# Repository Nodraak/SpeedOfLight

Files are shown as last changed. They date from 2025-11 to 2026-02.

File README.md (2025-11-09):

# Speed of light

*Reenactment of experiment(s) to measure the speed of light.*

Following a [video by AlphaPhenix in 2018](https://www.youtube.com/watch?v=YMO9uUsjXaI), where he redo Fizeau's experiement, I set out to reenact the experiement myself.
After some research, it seems to me that Foucault's experiement is easier to perform and will give a more precise value, while using a somehow similar technique.

(Incomplete) history of speed of light measurements from [Wikipedia](https://en.wikipedia.org/wiki/Speed_of_light#Measurement):

| Scientist | Experiment                                | Year | Value measured (accuracy)                  |
|-----------|-------------------------------------------|------|--------------------------------------------|
| Rømer     | Jupiter vs Io timing                      | 1676 | Earth's orbit's diameter / 22 min          |
| Bradley   | Aberration of light from a distant star   | 1729 | Sun to the Earth distance / 8 min 12 sec   |
| Fizeau    | Time of flight with a toothed wheel       | 1848 | 313 274 304 m/s (4.5%)                     |
| Foucault  | Time of flight with a mirror              | 1862 | 298 000 000 m/s (0.6%)                     |
| Cornu     | Refinement of Fizeau's                    | 1872 | 300 400 000 m/s (0.2%)                     |
| Michelson | Refinement of Foucault's                  | 1879 | 299 944 000 m/s (0.05%)                    |

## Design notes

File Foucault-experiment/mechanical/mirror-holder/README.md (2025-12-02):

# Mirror Holder

## Introduction

*Piece to hold the mirror and mount it on the motor, 70x40 mm.*

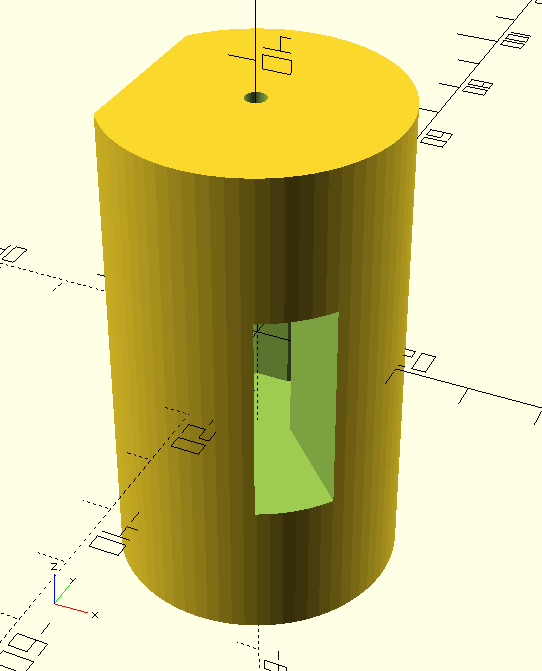
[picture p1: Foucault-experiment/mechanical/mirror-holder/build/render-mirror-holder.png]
Finished piece
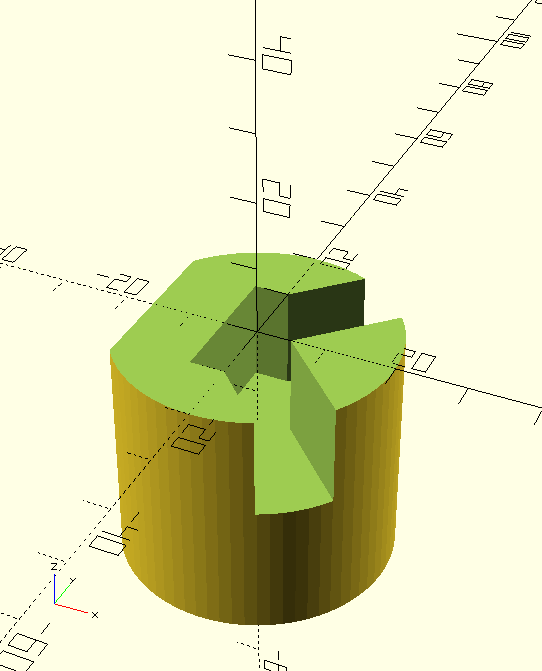
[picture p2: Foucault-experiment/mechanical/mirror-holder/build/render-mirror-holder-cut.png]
Half cut to view the inside
 

The holder will rotate quickly (10-100 RPM).
Therefore, the mirror must be well secured so that it does not fly away.
The best is to take advantage of the centrifugal force to keep it in place.
This leads to an unbalanced piece, which must then be carefully balanced with a notch of a very specific depth.
To help with balancing, the piece is as full as possible, and only a small path for the laser is carved through.

## Initial design with ChapGPT

An initial design was done with ChapGPT to quickly get started with a rough shape and to work around OpenScad's syntax which I'm not familiar with.

Prompt:

```
Write an openscad script code:

* Main: Create a main, vertical cylinder d=30 mm, h=60 mm
* Motor holes: Subtract at each end (top and bottom), a cylinder d=3 mm, h=15 mm
* Mirror: Subtract at the middle, a rectangles LxD=10x20 mm and h=30 mm
* Laser path:
    * Subtract two horizontal rectangles
        * W=sqrt(5**2+5**2) mm, L=20 mm
        * Each oriented +/- 45 deg horizontally compared to the previous middle rectangle
        * One end of the rectangle should be on the center of the main cylinder, the other end should go towards the outside
    * Subtract similar rectangles
        * But with the end +/- 5 mm horizontally from the center of the main cylinder
* Rear balancing: Subtract a rectangle H=60 mm, W=30 mm
    * Similar to the "Laser path" subtractions, but on the other side (horizontally)
    * Its center should be W/2+10 mm from the center of the Main cylinder

A few requests:

* Write only the code and nothing else.
* Do not add comments for obvious things, but do add a comment for each step above.
* Use variables as needed for constants.
* Add "$fn = 60;" at the top.
```

## 3D printing

* OpenScad
    * Render
    * Export as STL
* Ultimaker Cura
    * Layer height: 0.2 mm
    * Density: 40% (TBD: 30-50%?)
    * Pattern: Tri Hexagon (TBD: Cubic, Tri-Hexagonal, Grid, Triangle?)
    * Speed: 50 mm/sec
    * -> Print time: 4.5h (first PoC: 1.5h)

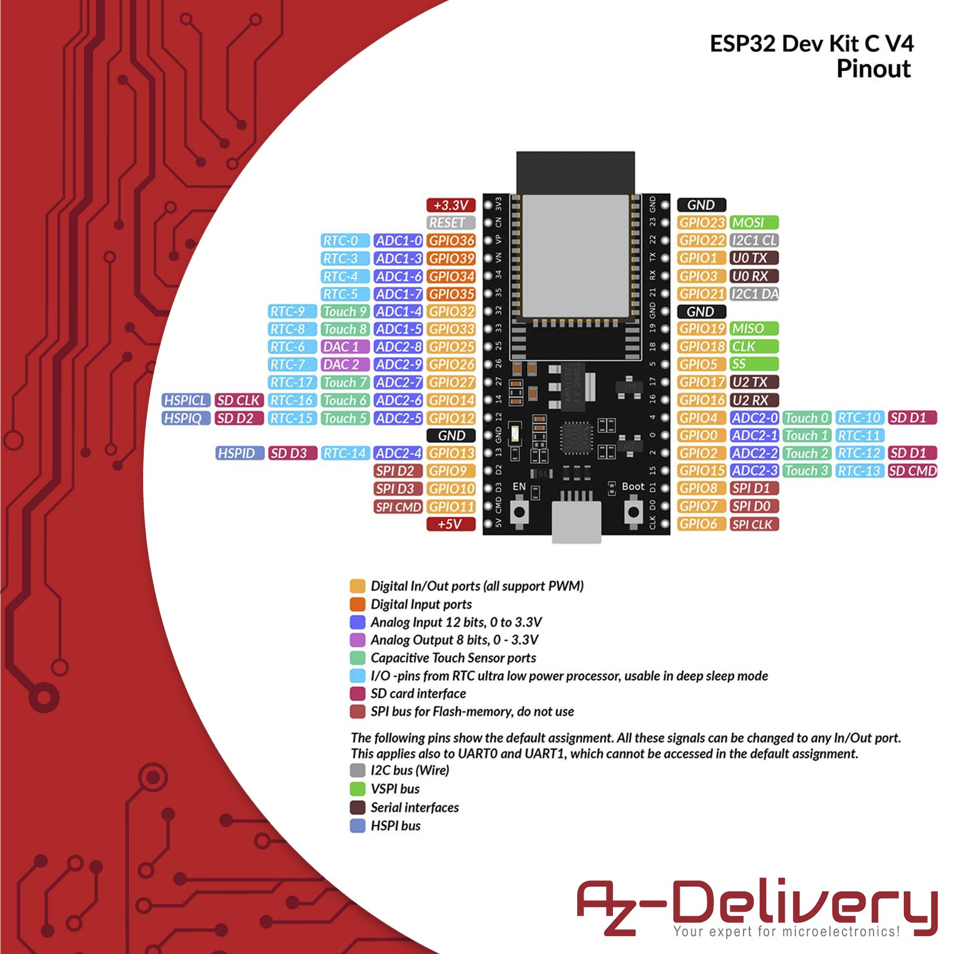
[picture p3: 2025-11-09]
Foucault-experiment/electrical/datasheets/pinout.jpg

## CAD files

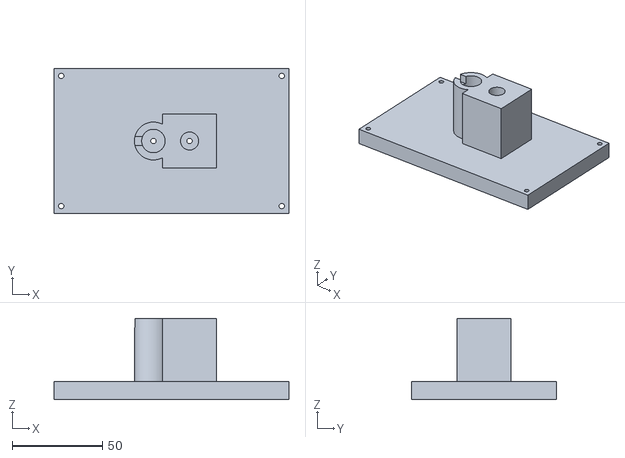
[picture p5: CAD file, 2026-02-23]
Foucault-experiment/mechanical/main-assembly/build/top-assembly.stl
130.0 x 80.0 x 45.0

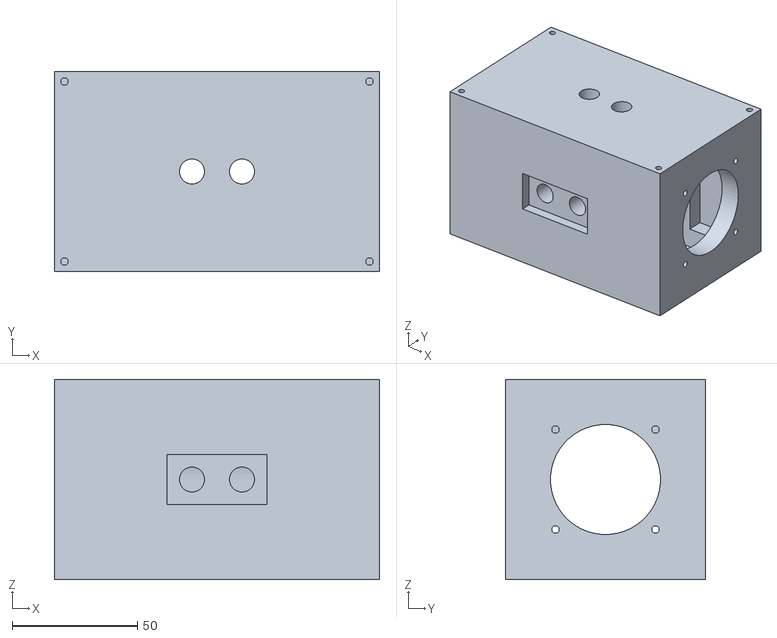
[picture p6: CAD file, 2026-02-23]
Foucault-experiment/mechanical/main-assembly/build/bottom-assembly.stl
130.0 x 80.0 x 80.0

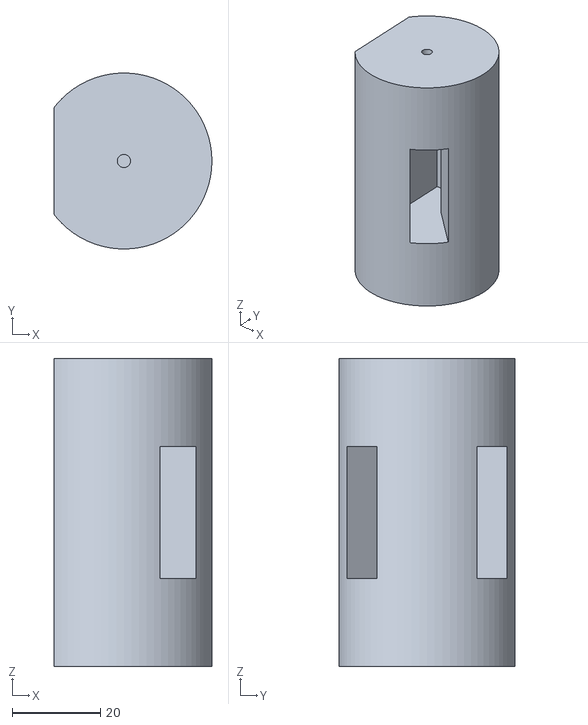
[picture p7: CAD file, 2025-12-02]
Foucault-experiment/mechanical/mirror-holder/build/mirror-holder.stl
35.9 x 40.0 x 70.0

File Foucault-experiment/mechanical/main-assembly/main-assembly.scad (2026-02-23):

/*
    # Main assembly

    Initial ChatGPT prompt:

    ```
    Write an openscad script code:

    * Create a rectangular box w=170 x d=80 x h=80. Write w=170 as 10+30+90+30+10
    * Difference a cylinder, centered in the rectangular box, of diameter=5+40+5
    * Difference a smaller rectangular box, depth=5+40+5, height=(80-(5+40+5))/2 + 5 + 5, just below the cylinder
    * Difference 4 holes on each side of the rectangular box, around the cylinder hole. diameter=3, d=10 further away than the cylinder's diameter.
    * Difference a vertical shaft (cylinder) from the rectangular box; d=10, centered on the depth axis, at an horizontal position of 10+30+90*1/4
    * Difference an horizontal shaft (cylinder) from the rectangular box; d=10, centered on the vertical axis, at an horizontal position of 10+30+90*1/4
    * Difference a vertical shaft (cylinder) from the rectangular box; d=10, centered on the depth axis, at an horizontal position of 10+30+90*3/4
    * Difference an horizontal shaft (cylinder) from the rectangular box; d=10, centered on the vertical axis, at an horizontal position of 10+30+90*3/4

    A few requests:

    * Write only the code and nothing else.
    * Do not add comments for obvious things, but do add a comment for each step above.
    * Use variables as needed for constants.
    * Add "$fn = 60;" at the top.
    ```
*/

// number of segments ; overrides $fa (minimum angle) and $fn (minimum size)
$fn = $preview ? 32 : 64;

//
// Constants
//

// main_box_w = 10 + 30 + 90 + 30 + 10;  // wall + motor + spinning cylinder + motor + wall
main_box_w = 10 + 30-10 + 70 + 30-10 + 10;  // wall + motor-wall + spinning cylinder + motor-wall + wall
main_box_h = 80;

main_cyl_d = 2 + 40 + 2; // 5 mm margin around spinning cylinder

motor_cube_depth = 20;
motor_cube_side = 60;

motor_screw_hole_pos = 40;
motor_screw_hole_d = 3;

// light_shaft_pos = 90*1/4;
light_shaft_pos = 40*1/4;
light_shaft_d = 10;
light_shaft_d_2 = 3;

laser_l = 45;  // 35 + some margin for the wire
laser_d = 13;  // 12 is too small
laser_box_d = laser_d + 2*4;

camera_pos = 40*1/4;
camera_holder_side = 30;
camera_holder_height = 45;

//
// Top assembly
//

module top_assembly() {
    translate([0, 0, main_box_h/2]) {
        // main plate
        difference() {

            // Create main plate
            translate([-main_box_w/2, -main_box_h/2, 0])
                cube([main_box_w, main_box_h, 10]);

            // 4 resting slots
            translate([0, 0, -main_box_h/2])
                bottom_assembly();

            // Vertical shaft at -1/4
            translate([-light_shaft_pos, 0, 0])
                cylinder(d = light_shaft_d_2, h = main_box_h + 2, center = true);

            // Vertical shaft at +1/4
            translate([+light_shaft_pos, 0, 0])
                cylinder(d = light_shaft_d_2, h = main_box_h + 2, center = true);

            // 4 screw holes - top
            for (x_offset = [-(main_box_w/2-5+1), +main_box_w/2-5+1])
                for (y_offset = [-(main_box_h/2-5+1), +main_box_h/2-5+1])
                    translate([x_offset, y_offset, 5])
                        cylinder(d = motor_screw_hole_d, h = 10+1, center = true);
        }

        // laser
        difference() {
            // laser holder
            translate([-light_shaft_pos, 0, laser_l/2])
                cylinder(d = laser_box_d, h = laser_l, center = true);

            // laser hole
            translate([-light_shaft_pos, 0, laser_l/2])
                cylinder(d = laser_d, h = laser_l+1, center = true);

            // wire
            translate([-light_shaft_pos-laser_box_d/2, 0, laser_l])
                cube([laser_box_d, 5, 2*5], center = true);
        }

        // camera
        difference() {
            // main block
            translate([+camera_pos, 0, laser_l/2])
                cube([camera_holder_side, camera_holder_side, camera_holder_height], center = true);

            // view hole
            translate([+camera_pos, 0, laser_l/2])
                cylinder(d = light_shaft_d, h = camera_holder_height+1, center = true);

            // laser hole
            translate([-light_shaft_pos, 0, laser_l/2])
                cylinder(d = laser_d, h = laser_l+1, center = true);
        }
    }
}

//
// Bottom assembly
//

module bottom_assembly() {
    difference() {

        // Create main rectangular box
        cube([main_box_w, main_box_h, main_box_h], center = true);

        rotate([0, 90, 0]) {
            // Difference main centered horizontal cylinder
            cylinder(d = main_cyl_d, h = main_box_w + 2, center = true);

            // centered horizontal rectangular box below cylinder
            translate([0, -main_cyl_d/2, -(main_box_w/2 - 10)])
                cube([main_box_h/2 + 1, main_cyl_d, main_box_w - 2*10]);

            // Sides motors attachement - cube
            translate([0, 0, -main_box_w/2 + 10 + motor_cube_depth/2 - 1])
                cube([motor_cube_side, motor_cube_side, motor_cube_depth], center = true);
            translate([0, 0, main_box_w/2 - 10 - motor_cube_depth/2])
                cube([motor_cube_side, motor_cube_side, motor_cube_depth], center = true);

            // 4 screw holes - on each side around cylinder hole
            for (x_offset = [-main_box_w/2, +main_box_w/2])
                for (y_offset = [-motor_screw_hole_pos/2, +motor_screw_hole_pos/2])
                    for (z_offset = [-motor_screw_hole_pos/2, +motor_screw_hole_pos/2])
                        translate([z_offset, y_offset, x_offset])
                            cylinder(d = motor_screw_hole_d, h = 2*10+1, center = true);
        }

        // Vertical shaft at -1/4
        translate([-light_shaft_pos, 0, 0])
            cylinder(d = light_shaft_d, h = main_box_h + 2, center = true);
        // Horizontal shaft at -1/4
        translate([-light_shaft_pos, -main_box_h/2, 0])
            rotate([90, 0, 0])
                cylinder(d = light_shaft_d, h = main_box_h + 2, center = true);

        // Vertical shaft at +1/4
        translate([+light_shaft_pos, 0, 0])
            cylinder(d = light_shaft_d, h = main_box_h + 2, center = true);
        // Horizontal shaft at +1/4
        translate([+light_shaft_pos, -main_box_h/2, 0])
            rotate([90, 0, 0])
                cylinder(d = light_shaft_d, h = main_box_h + 2, center = true);

        // resting slot - front
        translate([0, -main_box_h/2, 0])
            cube([40, 2*5, 20], center = true);

        // 4 resting slots - top
        for (x_offset = [-(main_box_w/2-5+1), +main_box_w/2-5+1])
            for (y_offset = [-(main_box_h/2-5+1), +main_box_h/2-5+1])
                translate([x_offset, y_offset, main_box_h/2-5])
                    cylinder(d = motor_screw_hole_d, h = 10+1, center = true);

        // cutout - side
        // translate([50, 0, 0])
        //     cube([100, 100, 100], center = true);

        // cutout - front
        // translate([0, -50, 0])
        //     cube([200, 100, 100], center = true);
    }
}

//
// Main
//

top_assembly();
bottom_assembly();

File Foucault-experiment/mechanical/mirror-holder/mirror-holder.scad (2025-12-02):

/*
    Mirror holder
*/

$fn = 72;

echo("==========");

//
// Helpers
//

function r2d(r) = r * 180 / 3.14159;
function d2r(d) = d * 3.14159 / 180;

pi_deg = acos(-1);
echo("pi_deg", pi_deg);

delta = 99;

//
// Constants
//

d_main = 40; // arbitrary
r_main = d_main / 2;

mirror_L = 10; // space
mirror_D = 22; // spec
mirror_H = 30; // spec

d_hole = 3; // spec
h_hole = 12.5; // spec
h_hole_margin = 2.5 + 5;

h_main = mirror_H + 2 * (h_hole + h_hole_margin);
echo("h_main", h_main);

laser_W = sqrt(5*5 + 5*5);
laser_L = delta;
laser_offset = 5;

rear_cap_h = 4.12; // manual optim COG
rear_W = d_main;
rear_H = h_main + delta;

// rear_cap_h 4.15 = COG base estimated 1.01, reality 1.03
// => better rear_cap_h 4.12 (-0.006)

//
// Main cylinder
//

difference() {
    cylinder(h = h_main, d = d_main, center = true);

    // Motor holes
    m_h = mirror_H/2 + h_hole_margin + h_hole/2;
    translate([0, 0, m_h]) cylinder(h = h_hole+1, d = d_hole, center = true);
    translate([0, 0, -m_h]) cylinder(h = h_hole+1, d = d_hole, center = true);

    // Mirror
    cube([mirror_L, mirror_D, mirror_H], center = true);

    // Laser path - center
    rotate([0, 0, 45]) translate([0, -laser_W/2, -mirror_H/2]) cube([laser_L, laser_W, mirror_H]);
    rotate([0, 0, -45]) translate([0, -laser_W/2, -mirror_H/2]) cube([laser_L, laser_W, mirror_H]);

    // Laser path - offset
    translate([0, laser_offset, 0])
        rotate([0, 0, 45]) translate([0, -laser_W/2, -mirror_H/2]) cube([laser_L, laser_W, mirror_H]);
    translate([0, -laser_offset, 0])
        rotate([0, 0, -45]) translate([0, -laser_W/2, -mirror_H/2]) cube([laser_L, laser_W, mirror_H]);

    // Rear balancing
    translate([-rear_W-r_main+rear_cap_h, -rear_W/2, -rear_H/2]) cube([rear_W, rear_W, rear_H]);

    // DEBUG: cut in half
    // translate([-50, -50, 0])
    //    cube([100, 100, 100]);
}

//
// Check COG
//

// cog_mirror
cog_mirror = -1.36;

// cog_base
theta_deg = 2*acos((r_main -rear_cap_h)/r_main );
// The centroid x of the remaining shape (signed toward the side opposite the removed cap)
cog_base = 2 * r_main * sin(theta_deg / 2)^3 / (3 * (3.14159 - 0.5*(d2r(theta_deg)-sin(theta_deg))));
echo("cog_base", cog_base);

// cog_base = 1.03;

// result
cog_global = (2 * (h_hole + h_hole_margin) * cog_base + mirror_H * cog_mirror) / h_main;

echo("Estimated COG:", cog_global);

echo("==========");

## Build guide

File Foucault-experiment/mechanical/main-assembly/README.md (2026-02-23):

# Main Assembly (Top + Bottom pieces)

## Introduction

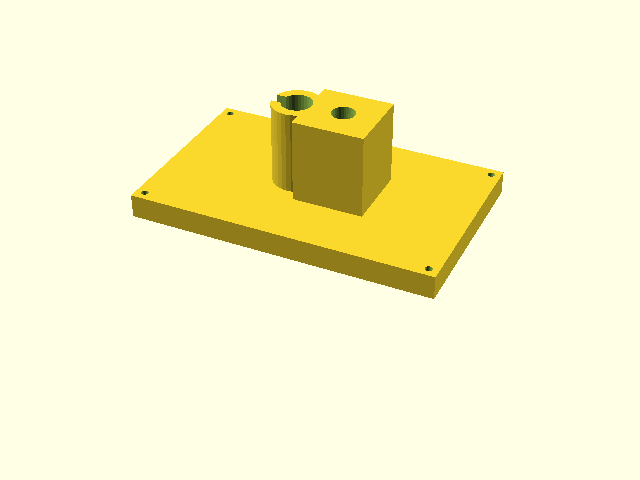
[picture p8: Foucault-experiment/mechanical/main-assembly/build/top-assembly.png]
Top assembly
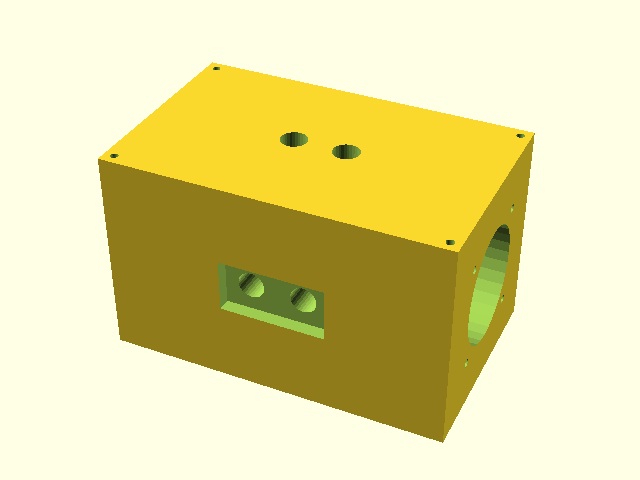
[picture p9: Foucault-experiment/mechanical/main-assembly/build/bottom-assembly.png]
Bottom assembly


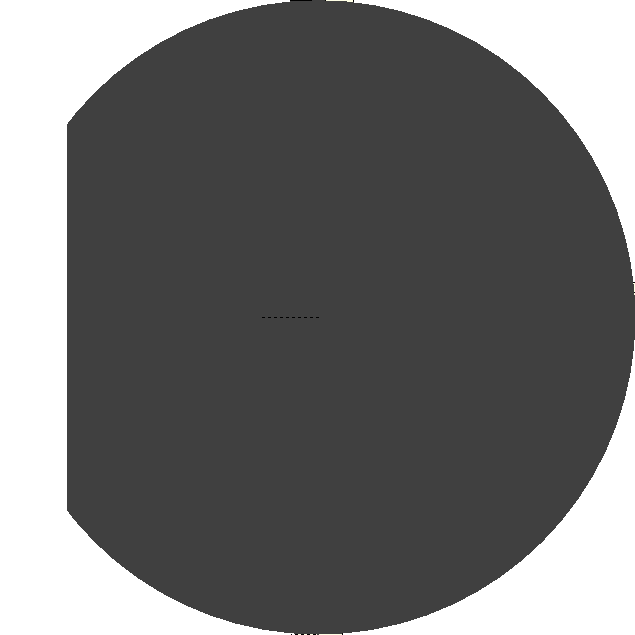
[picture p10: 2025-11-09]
Foucault-experiment/mechanical/mirror-holder/build/cog-slice-mirror-base-40-4.15.png

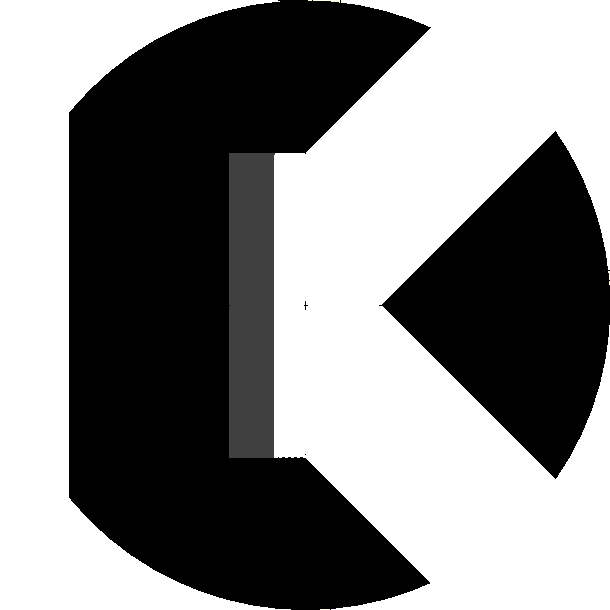
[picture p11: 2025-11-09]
Foucault-experiment/mechanical/mirror-holder/build/cog-slice-mirror-laser.png

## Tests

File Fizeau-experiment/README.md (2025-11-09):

# Fizeau's Experiment

*Some preliminary notes on Fizeau's experiment.*

## Laser

* Power: 5 mW
* Divergence: TBD

Safety:

* MPE = W/cm2 = safe
* Fully open pupil = 0.39 cm2
* MPE = 1 mW/cm2

## Distance and timing

300 000 000 m/s = 300 m/us

2 *  150 m =>  1 us
2 * 1.5 km => 10 us
2 * 8.0 km => 50 us

* Mueggelsee: 2 * 3.4 km
* Maerchenland: 2 * 1.5 km
* Kanal: 2 * 1.5 km
* Treptower: 2 * 1.0 km
* Havel: 2 * 3.5 km
* Saatwinkler Damm: 2 * 3.8 km

* Lehnitzsee: 2 * 2.0 km

* Trebeurden 1: 2 * 1.0 km
* Trebeurden 2: 2 * 3.7 km
* Trebeurden 3: 2 * 8.0 km

## Wheel

* Fizeau: 720 teeth / 15-50 rps
* AlphaPhenix: 140 teeth wheel (10 cm?) / 2-10 k rpm = 40-200 rps
    * => 10-50 k teeth/sec

* 10 k mm / sec = 1 mm / 100 us
* 50 k mm / sec = 1 mm /  20 us

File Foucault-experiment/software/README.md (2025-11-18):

# Software

## Introduction

Functions:

* Control the motor/ESC
    * Input from stdin: 1-100 k RPM
    * Create the PWM
        * 50 Hz: 20 ms idle, 1-2 ms signal
        * Precision: 1 % (10 us = 2 400 clock ticks at 240 MHz)
* Measure the actual RPM
    * Read the diode (analog) and detect discontinuity in the signal
    * 100 k RPM, 100 samples / rotation = 16 000 samples/sec = 60 us / sample
    * At 240 MHz, that's 15 000 clock ticks / sample
    * Print result at 1 Hz: RPM count, min/max duration between two discontinuities (for quality check)

## Arduino IDE for ESP32

azdelivery esp32 devkitc v4

CPU: Xtensa dual-core 32-bit LX6 microprocessor, 240 MHz
Memory: 520 KiB RAM
ADC: 2 × 12-bit SAR ADCs, up to 18 channels, with four levels of attenuation

https://github.com/tombenke/darduino

* Select Tools > Board > Boards Manager from the Arduino IDE menus to open the "Boards Manager" view in the left side panel.
* Scroll down through the list of boards platforms until you see the "esp32 by Espressif Systems" entry.
* Click the "INSTALL" button at the bottom of the entry.
* Wait for the installation to finish.

```
I need a C code to run on an azdelivery esp32 devkitc v4, via the Arduino IDE, with the following functions:

* Control the motor/ESC
    * Input from stdin: read stdin, parse an int between 1 000 and 100 000 (RPM)
    * Create the PWM:
        * Digital output
        * (50 Hz: 20 ms idle, 1-2 ms signal)
        * Precision: 1 % (10 us = 2 400 clock ticks at 240 MHz)
            * Can we implement it in the main loop? Do we need to use IRQs? Are they timers or builtin PWM controller on the ESP32?
    * Dont forget the arming sequence of the ESC
* Measure the actual RPM
    * Read the diode signal (analog input) and detect discontinuity in the signal to detect one rotation
        * In oder to do that in a reliable way, we can use an adaptive threshold:
        * Prepare an array of say, 256 values initialised to 0
        * Each time a value is read, increment the corresponding cell
        * After a 1 second cycle, find out the median value
        * Use this median value as the threshold for the next 1 sec cycle
        * Keep track of when we are in or out of reading a signal, to not count multiple times a given signal (wait for it to go back down below the threshold)
    * Measure per-sample timing (ISR execution time profiling) with a 1024 array (histogram), with 1 us per cell (1-1000 us)
        * Print at 1 Hz statistics: 10 deciles values
    * Also measure rotation duration with a 1024 items array (scale it so that index 512 corresponds to the expect duration at the currently configured ESC RPM, and index 0 and 1023 correspond to x1/10 and x10 this value)
    * Precision: 100 k RPM, 100 samples / rotation = 170 000 samples/sec = 6 us / sample
        * (At 240 MHz, that's 15 000 clock ticks / sample)
        * Same question again: can we implement it in the main loop? Do we need to use IRQs? Are they timers or builtin PWM controller on the ESP32?
    * Print the result at 1 Hz: RPM count, the threshold value, and other statistics as needed
* Use pin 32 for the PWM and 33 for the ADC input
```

## Example output (on Linux)

```
$ ./a.out

+---------------------------------+
| Project F - Foucault experiment |
+---------------------------------+

nod_pwm_init: pin=32 freq=50
nod_pwm_write_us: pin=32 freq=50 duty_us=1000
nod_pwm_write_duty: pin=32 duty=0
nod_adc1_init: ch=5
nod_mutex_init
nod_pwm_write_us: pin=32 freq=50 duty_us=1000
nod_pwm_write_duty: pin=32 duty=0
nod_timer_init: frequency=1000000 alarm_value=16000

cmd_rpm =   1000 RPM ; rev dur =  62500 us
meas_rpm =   1980 RPM ; rev dur =  30303 us
threshold_index = 1510 [0-4096] = 1.843 V
/--- sample_hist
| sample_total_count=  1824
| min=     0 | med=   518 | max=  2973
| ds=    184    268    347    433    518    596    685    762    838   2973
\---
/--- rev_duration
| sample_total_count=  1824
| min=  1040 | med=  1104 | max=  1209
| ds=   1075   1076   1083   1099   1104   1108   1109   1110   1111   1209
\---
/--- irq_duration
| sample_total_count=  1824
| min=     0 | med=     5 | max=    93
| ds=      2      3      5      5      5      5      5      6      6     93
\---

cmd_rpm =   1000 RPM ; rev dur =  62500 us
meas_rpm =   3060 RPM ; rev dur =  19607 us
threshold_index = 1485 [0-4096] = 1.813 V
/--- sample_hist
| sample_total_count=   917
| min=     0 | med=   525 | max=  2973
| ds=    184    268    357    436    525    609    687    768    838   2973
\---
/--- rev_duration
| sample_total_count=   917
| min=  1036 | med=  1077 | max=  1555
| ds=   1074   1075   1075   1076   1077   1097   1107   1110   1111   1555
\---
/--- irq_duration
| sample_total_count=   917
| min=     0 | med=     3 | max=    27
| ds=      2      2      2      3      3      5      5      5      6     27
\---
```

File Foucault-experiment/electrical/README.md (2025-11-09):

# Electrical

## Introduction

*A small PCB to connect all the components cleanly, 80x100 mm.*

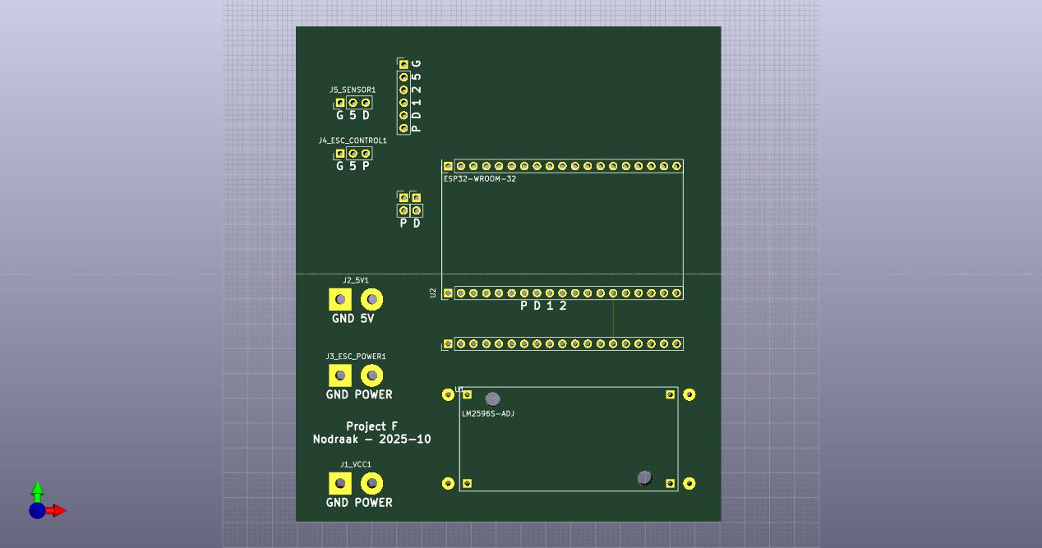
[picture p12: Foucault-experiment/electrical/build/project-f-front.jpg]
3D PCB view, front
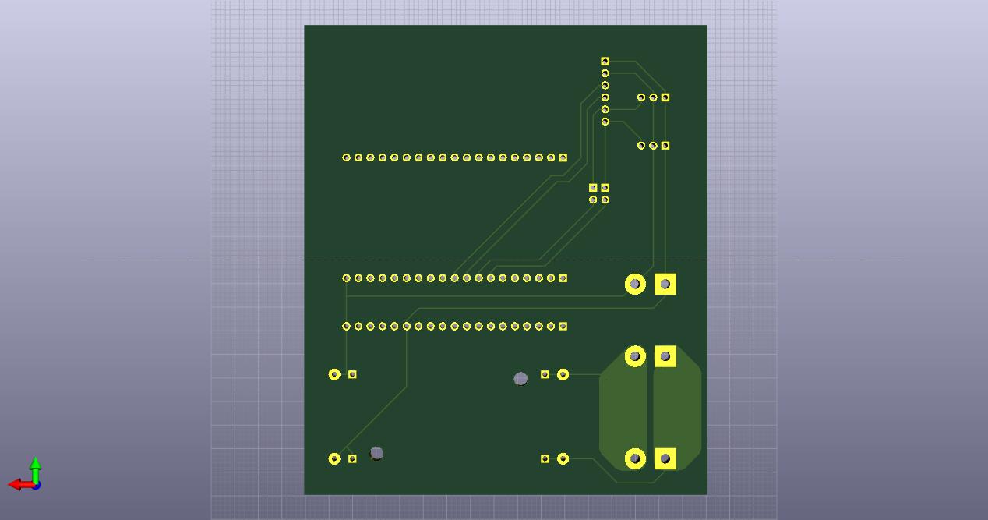
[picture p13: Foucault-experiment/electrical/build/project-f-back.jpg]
3D PCB view, back
 

The following components will be used:

* Electric motor + ESC: Power (12V), PWM
* Light sensor: Power, signal
* ESP32 (5V)
* Step down 12V to 5V

## Notes

### MCU

* ESP32 WROOM 32
* AZ Delivery ESP32 DevKitC v4

### KY-018

LDR-resistor (Light dependent resistor), which decreases its resistance at brighter surrounding

Pinout:
* GND
* V+ (5V)
* Signal

```c
int rawValue = analogRead(sensorPin);
float voltage_v = rawValue * (5.0 / 1023);
float resistance = 10 * voltage_v / ( 5.0 - voltage_v);
```

### ESC

Power rating:

* Max 150 W -> @12 V = 12 A
* Max 13 A for 60 sec

PWM control:

50 Hz PWM (20 ms): 20 ms low + 1-2 ms active

### PSU

* Wall mounted: 12 V * 2 A = 24 W
* Lab: 30 V * 10 A = 300 W

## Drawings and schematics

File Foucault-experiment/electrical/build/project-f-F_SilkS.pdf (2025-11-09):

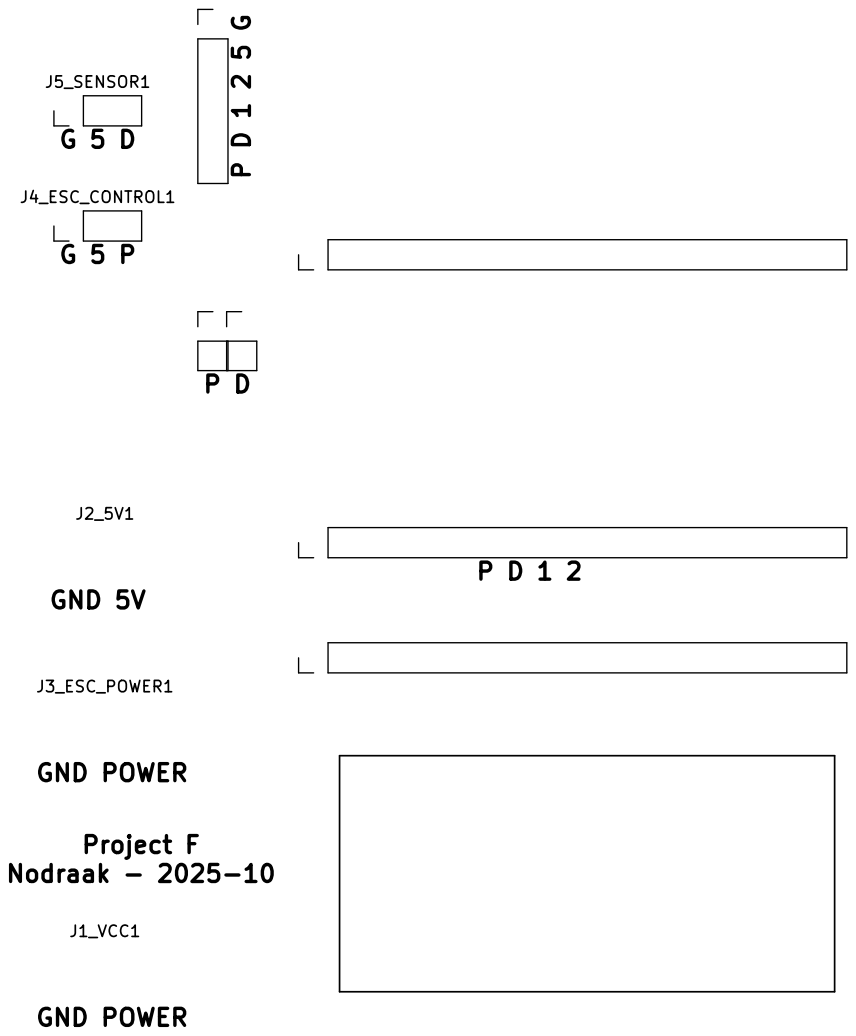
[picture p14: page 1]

GND POWER GND POWER GND 5V G 5 P G 5 D

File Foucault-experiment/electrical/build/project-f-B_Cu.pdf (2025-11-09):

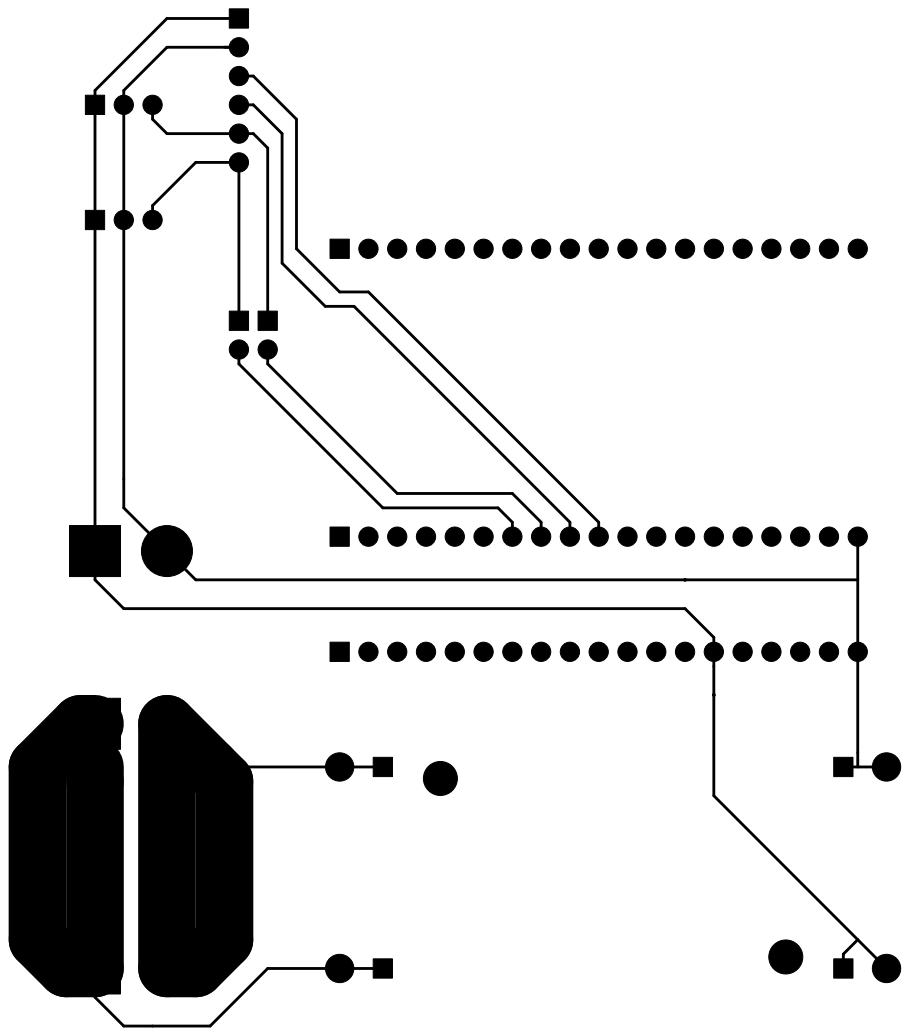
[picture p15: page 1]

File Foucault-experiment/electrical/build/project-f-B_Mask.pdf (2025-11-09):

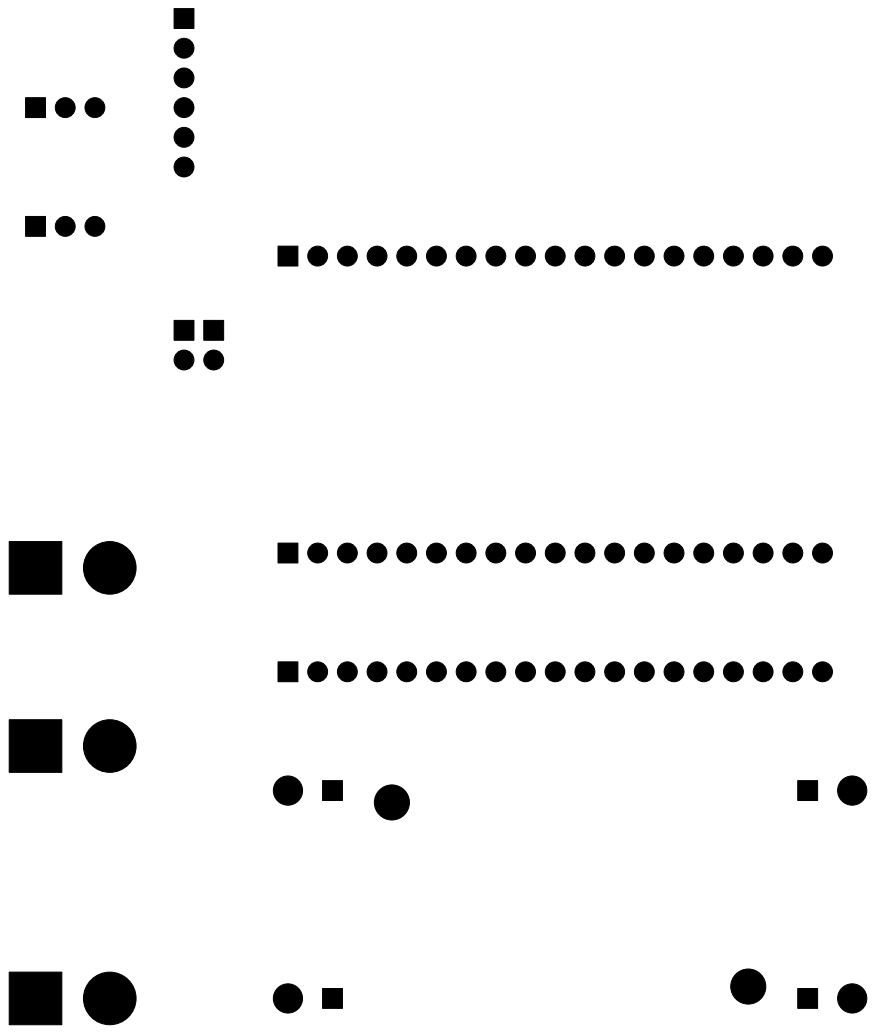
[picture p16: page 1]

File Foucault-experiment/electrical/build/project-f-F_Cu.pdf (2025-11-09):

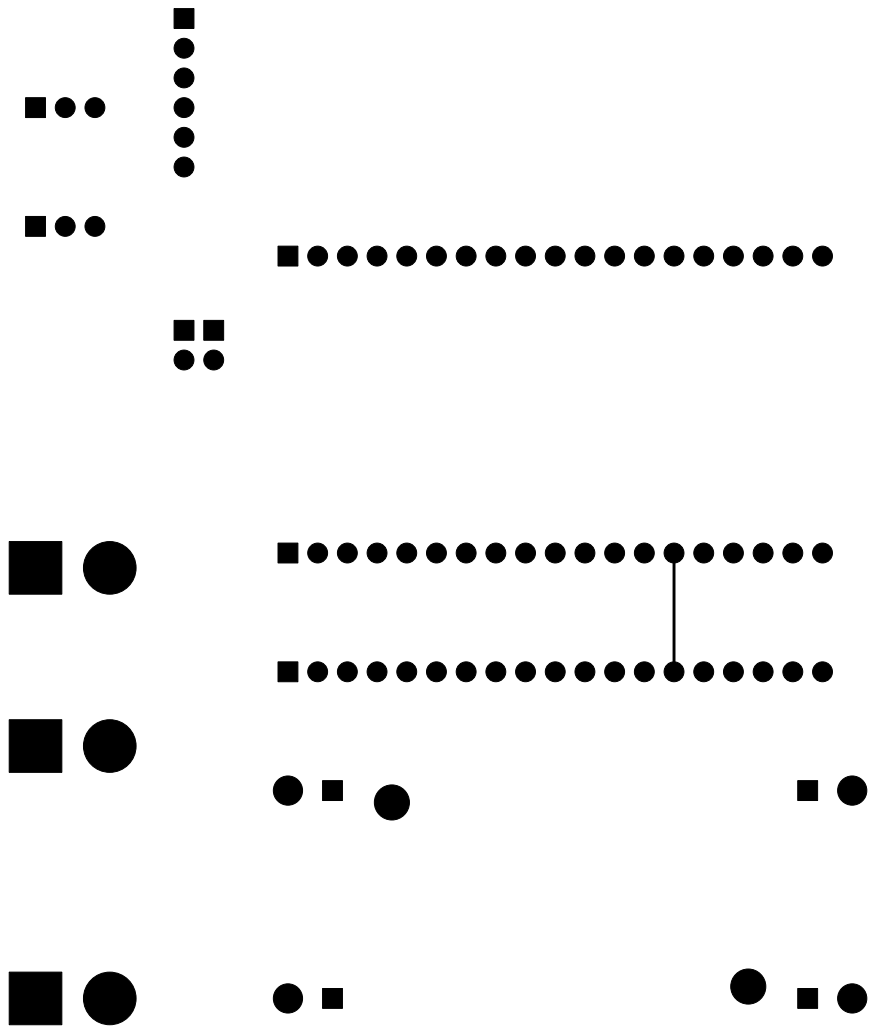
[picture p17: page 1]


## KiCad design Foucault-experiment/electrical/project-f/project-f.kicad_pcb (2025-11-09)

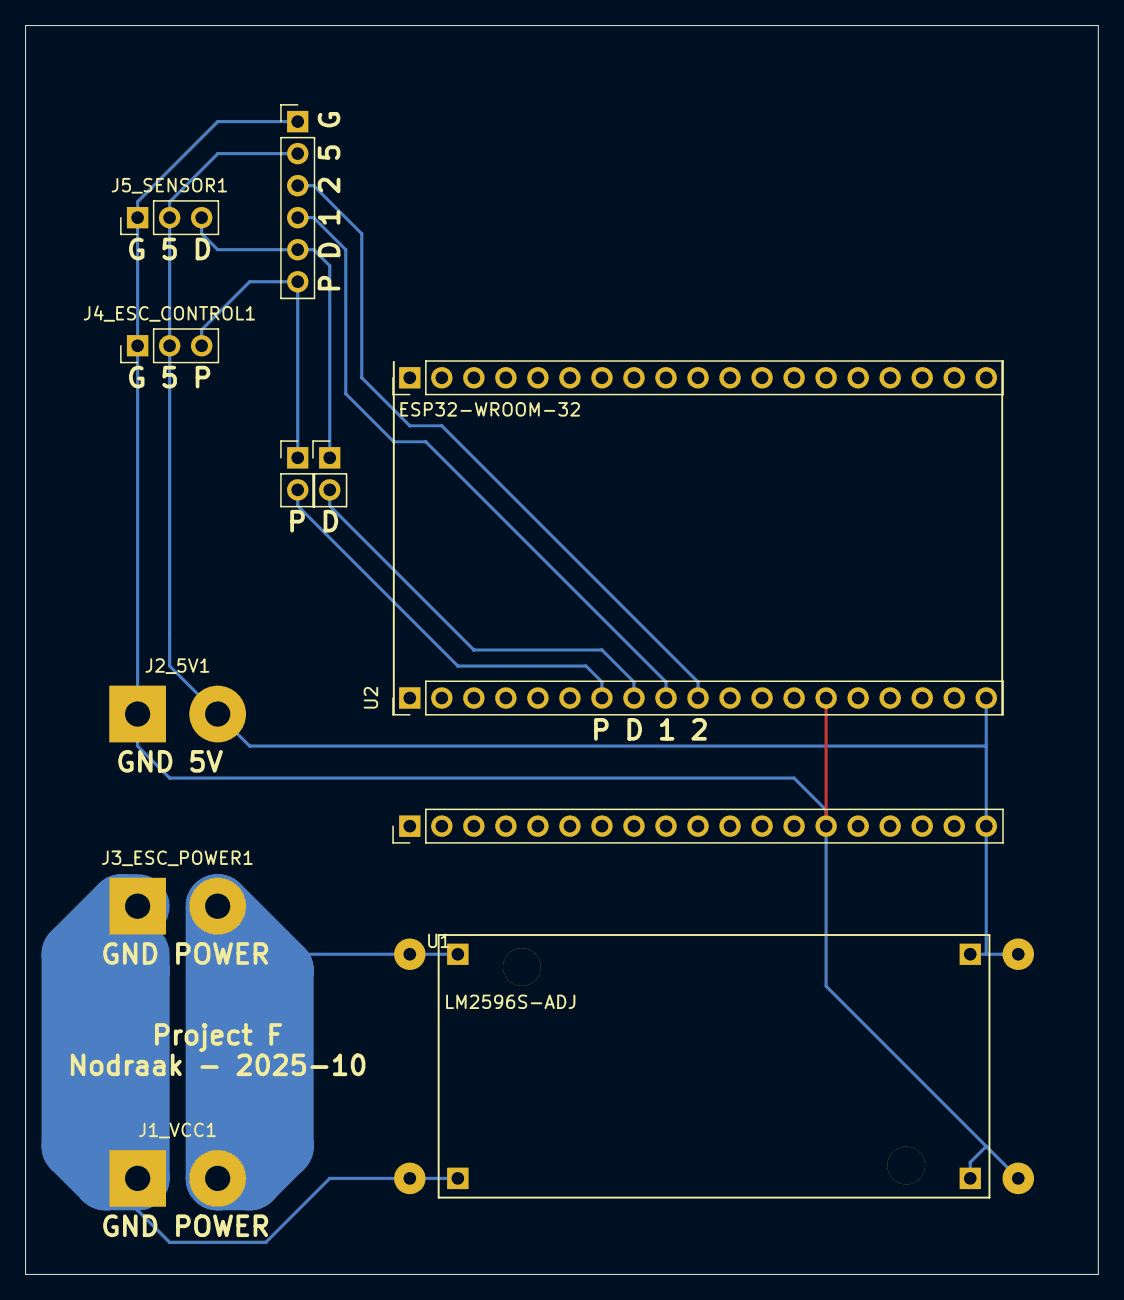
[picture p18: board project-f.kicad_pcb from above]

Board: 2 copper layers, 85.1 x 99.1 mm, 7 parts (0 on the bottom side), 6 nets.

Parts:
J1_VCC1, J2_5V1, J3_ESC_POWER1: Conn_01x02; SolderWirePad_1x02_P7.62mm_Drill2mm
J4_ESC_CONTROL1, J5_SENSOR1: Conn_01x03; PinHeader_1x03_P2.54mm_Vertical
U1: LM2596S-ADJ; AZ-LM2596S
U2: ESP32-WROOM-32; ESP32_DevkitC

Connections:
+5V: J2_5V1.2, J4_ESC_CONTROL1.2, J5_SENSOR1.2, U1.4, U2.2
+VDC: J1_VCC1.2, J3_ESC_POWER1.2, U1.1
/ESC_PWM: J4_ESC_CONTROL1.3, U2.8
/Sensor_signal: J5_SENSOR1.3, U2.9
GND: J2_5V1.1, J4_ESC_CONTROL1.1, J5_SENSOR1.1, U1.2, U2.1, U2.15, U2.38
GNDPWR: J1_VCC1.1, J3_ESC_POWER1.1, U1.3

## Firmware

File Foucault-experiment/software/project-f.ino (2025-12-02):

#include "nod_hal.h"
#include "nod_stats.h"

#include <stdint.h>
#include <stdlib.h>
#include <string.h>

// ----------------------- User config -----------------------

#define SERIAL_BAUD     115200

#define PWM_PIN         NOD_PWM_GPIO_32
#define ADC_PIN         NOD_ADC1_GPIO_33

#define PWM_FREQ_HZ     50
#define PWM_MIN_US      1000
#define PWM_MAX_US      2000

#define TIMER_FREQUENCY (1000 * 1000)
#define SAMPLES_PER_REV 1000

#define REV_MIN_RPM     100
#define REV_MAX_RPM     (1000*1000) // ADC 4 k RPM ; GPIO IRQ 1200 k RPM

// ADC with continuous sampling and threshold:
//   Angular resolution needed:
//   1 part per pi*D ; D = 200 mm => 1 part per 600
//   => Aim for 1/1000
//   Req for 100 k RPM * 1000 samples/rev => 1.5 M samples/sec = 0.7 us/sample
//   Realistic adc + irq -> 15 us = 66 KHz
//   66 KHz / 1000 samples/rev => 4000 RPM max
//   => impossible
// GPIO + IRQ:
//   gpio + irq -> 5 us = 200 KHz = 1200 k RPM

#define SAMPLE_HIST_BINS    4096  // Map 0-4096 (resolution 12 bits hardcoded) (0-5 V)
#define REV_HIST_BINS       4096  // Map 0-4096 ms (1-100 k RPM = 0.6 - 60 ms)
#define IRQ_HIST_BINS       4096  // Map 0-4096 us

#define PRINT_CYCLE_SEC     1.000

// ----------------------- Globals -----------------------

nod_mutex_t timer_mutex = {0};

// written by IRQ, needs volatile
volatile uint32_t sample_hist_irq[SAMPLE_HIST_BINS] = {0}; // To determine rev threshold
volatile uint32_t rev_duration_hist_irq[REV_HIST_BINS] = {0}; // Make sure rev count is clean and reliable
volatile uint32_t irq_duration_hist_irq[IRQ_HIST_BINS] = {0}; // Measure adc read duration

// only read by IRQ
uint32_t threshold_index_irq = 0;
uint32_t rev_count_irq = 0;

// ----------------------- Utilities -----------------------

uint32_t nod_rpm_to_pulse_us(uint32_t rpm)
{
    const uint32_t rpm_clamped = (rpm < REV_MIN_RPM) ? REV_MIN_RPM : (rpm > REV_MAX_RPM) ? REV_MAX_RPM : rpm;
    return PWM_MIN_US + (rpm_clamped - REV_MIN_RPM) * (PWM_MAX_US - PWM_MIN_US) / (REV_MAX_RPM - REV_MIN_RPM);
}

void nod_esc_arm(void)
{
    nod_printf("Arming ESC...\n");

    // Option A: standard low-high-low
    nod_pwm_write_us(PWM_PIN, PWM_FREQ_HZ, PWM_MIN_US);
    nod_time_sleep_sec(2.000);
    nod_pwm_write_us(PWM_PIN, PWM_FREQ_HZ, PWM_MAX_US);
    nod_time_sleep_sec(2.000);
    nod_pwm_write_us(PWM_PIN, PWM_FREQ_HZ, PWM_MIN_US);
    nod_time_sleep_sec(2.000);
    nod_printf("ESC armed (standard sequence)\n");

    /*
    // Option B: simple safe-low only
    nod_pwm_write_us(PWM_PIN, PWM_FREQ_HZ, PWM_MIN_US);
    nod_time_sleep_sec(3.000);
    nod_printf("ESC armed (safe-low only)\n");
    */
}

// ----------------------- ISR -----------------------

void NOD_IRAM_ATTR nod_timer_irq(void)
{
    static bool last_sample_above_threshold = false;
    static uint32_t rev_start_us_last = 0;

    nod_mutex_lock(&timer_mutex);

    const uint32_t start_us = nod_time_get_us();

    // read sample
    const uint32_t adc_raw = nod_adc1_read(ADC_PIN);
    const uint32_t sample_index = adc_raw;
    if (0 <= sample_index && sample_index < SAMPLE_HIST_BINS)
    {
        sample_hist_irq[sample_index] ++;
    }

    // crossing detection with basic debounce
    if (sample_index >= threshold_index_irq)
    {
        if (last_sample_above_threshold == false)
        {
            last_sample_above_threshold = true;

            rev_count_irq++;

            // compute rev duration
            const uint32_t rev_duration_us = start_us - rev_start_us_last;
            const uint32_t rev_duration_index = rev_duration_us / 1000;
            if (0 <= rev_duration_index && rev_duration_index < REV_HIST_BINS)
            {
                rev_duration_hist_irq[rev_duration_index] ++;
            }
            rev_start_us_last = start_us;
        }
    }
    else
    {
        last_sample_above_threshold = false;
    }

    // ISR timing profiling
    const uint32_t dur_us = nod_time_get_us() - start_us;
    const uint32_t dur_index = dur_us;
    if (0 <= dur_index && dur_index < IRQ_HIST_BINS)
    {
        irq_duration_hist_irq[dur_index]++;
    }

    nod_mutex_unlock(&timer_mutex);
}

// ----------------------- Main -----------------------

uint32_t mapper(uint32_t param)
{
    return param;
}

int main(void)
{
    nod_time_init();

    nod_stdout_init(SERIAL_BAUD);

    nod_time_sleep_sec(1.000);
    nod_printf("\n");
    nod_printf("+---------------------------------+\n");
    nod_printf("| Project F - Foucault experiment |\n");
    nod_printf("+---------------------------------+\n");
    nod_printf("\n");
    nod_time_sleep_sec(1.000);

    nod_pwm_init(PWM_PIN, PWM_FREQ_HZ);
    nod_pwm_write_us(PWM_PIN, PWM_FREQ_HZ, PWM_MIN_US);

    nod_adc1_init(ADC_PIN);

    nod_mutex_init(&timer_mutex);

    // start motor control and rev counting

    threshold_index_irq = SAMPLE_HIST_BINS/2;  // init to average
    uint32_t rpm_command = 1200;

    nod_esc_arm();

    nod_pwm_write_us(PWM_PIN, PWM_FREQ_HZ, nod_rpm_to_pulse_us(rpm_command));

    nod_timer_t timer;
    nod_timer_init(
        &timer,
        TIMER_FREQUENCY,
        /* callback_period_sec */ 1 / (SAMPLES_PER_REV * (rpm_command / 60)) /* => 1 K RPM * 1000 sample / revolution = 60 us */,
        &nod_timer_irq
    );

    double last_print_sec = nod_time_get_sec();
    while (true)
    {
        //
        // Read serial input
        //

        char buf[128] = "";

        while (nod_stdin_peek())
        {
            const char c = nod_stdin_read();
            if (c == '\r')
            {
                continue;
            }

            if (c == '\n')
            {
                rpm_command = atoi(buf);
                buf[0] = '\0';

                // Update PWM
                if (rpm_command / 60 == 0)
                    rpm_command = 60;
                nod_printf("cmd_rpm = %d RPM ; rev dur = %d us\n", rpm_command, 1000 * 1000 / (rpm_command / 60));
                nod_pwm_write_us(PWM_PIN, PWM_FREQ_HZ, nod_rpm_to_pulse_us(rpm_command));
            }
            else
            {
                const uint32_t len = strlen(buf);
                buf[len] = c;
                buf[len + 1] = '\0';
            }
        }

        //
        // 1 Hz status print
        //

        const double now_sec = nod_time_get_sec();

        if (now_sec - last_print_sec >= PRINT_CYCLE_SEC)
        {
            ///
            // copy IRQ-owned data to local working copy, and reset IRQ copy
            ///

            nod_mutex_lock(&timer_mutex);

            static uint32_t sample_hist_thread[SAMPLE_HIST_BINS] = {0}; // To determine rev threshold
            static uint32_t rev_duration_hist_thread[REV_HIST_BINS] = {0}; // Make sure rev count is clean and reliable
            static uint32_t irq_duration_hist_thread[IRQ_HIST_BINS] = {0}; // Measure adc read duration

            uint32_t rev_count_thread = rev_count_irq;

            memcpy(sample_hist_thread, (uint32_t*)sample_hist_irq, sizeof(sample_hist_irq));
            memcpy(rev_duration_hist_thread, (uint32_t*)rev_duration_hist_irq, sizeof(rev_duration_hist_irq));
            memcpy(irq_duration_hist_thread, (uint32_t*)irq_duration_hist_irq, sizeof(irq_duration_hist_irq));

            rev_count_irq = 0;

            memset((uint32_t*)sample_hist_irq, 0, sizeof(sample_hist_irq));
            memset((uint32_t*)rev_duration_hist_irq, 0, sizeof(rev_duration_hist_irq));
            memset((uint32_t*)irq_duration_hist_irq, 0, sizeof(irq_duration_hist_irq));

            nod_mutex_unlock(&timer_mutex);

            //
            // Fancy weighted average => seems ok?, but complex
            //

            uint32_t sum_below_threshold = threshold_index_irq;
            uint32_t sample_total_count_below_threshold = 1; //  avoid div by zero
            for (uint32_t i = 0; i < threshold_index_irq; i++)
            {
                sum_below_threshold += i * sample_hist_thread[i];
                sample_total_count_below_threshold += sample_hist_thread[i];
            }
            const uint32_t average_below = sum_below_threshold / sample_total_count_below_threshold;

            uint32_t sum_above_threshold = threshold_index_irq;
            uint32_t sample_total_count_above_threshold = 1; //  avoid div by zero
            for (uint32_t i = threshold_index_irq; i < SAMPLE_HIST_BINS; i++)
            {
                sum_above_threshold += i * sample_hist_thread[i];
                sample_total_count_above_threshold += sample_hist_thread[i];
            }
            const uint32_t average_above = sum_above_threshold / sample_total_count_above_threshold;

            const float percent_below = 1.0 * sample_total_count_below_threshold / (sample_total_count_below_threshold + sample_total_count_above_threshold);

            const uint32_t average = (average_below + average_above) / 2;

            threshold_index_irq = average;

            //
            // print
            //

            nod_printf("\n");

            if (rpm_command / 60 == 0)
                rpm_command = 60;

            if (rev_count_thread == 0)
                rev_count_thread = 1;

            nod_printf("cmd_rpm  = %7.3f k RPM ; cmd_rev_dur  = %7.3f ms\n", rpm_command / 1000.0, 1000.0 / (rpm_command / 60.0));
            nod_printf("meas_rpm = %7.3f k RPM ; meas_rev_dur = %7.3f ms\n", rev_count_thread * 60.0 / 1000.0, 1000.0 / rev_count_thread);
            nod_printf(
                "threshold_index_irq = %4d [0-%d] = %5.3f V // samples: %.1f%% < threshold < %.1f%%\n",
                threshold_index_irq, SAMPLE_HIST_BINS, threshold_index_irq * 5.0 / SAMPLE_HIST_BINS, 100 * percent_below, 100 - 100 * percent_below
            );

            // print sample stats

            struct nod_stats_t stats_sample_hist = {0};
            nod_stats_init(&stats_sample_hist, sample_hist_thread, SAMPLE_HIST_BINS, mapper, mapper);
            nod_stats_print(&stats_sample_hist, "sample_hist (adc raw: 0-4096)");

            // print rev duration stats

            struct nod_stats_t stats_rev_duration = {0};
            nod_stats_init(&stats_rev_duration, rev_duration_hist_thread, REV_HIST_BINS, mapper, mapper);
            nod_stats_print(&stats_rev_duration, "rev_duration (ms) (1 k RPM = 60 ms ; 100 k RPM = 0.6 ms)");

            // print IRQ duration stats

            struct nod_stats_t stats_irq_duration = {0};
            nod_stats_init(&stats_irq_duration, irq_duration_hist_thread, IRQ_HIST_BINS, mapper, mapper);
            nod_stats_print(&stats_irq_duration, "irq_duration (us) (100 k RPM * 1000 samples/rev = 0.7 us ; Realistic ESP32 = 15 us");

            nod_printf("\n");

            last_print_sec += 1.000;
        }

        nod_time_sleep_sec(0.001);
    }

    return 0;
}

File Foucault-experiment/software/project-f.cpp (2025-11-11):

#include "nod_hal.h"

#include <stdint.h>

// ----------------------- User config -----------------------

#define SERIAL_BAUD     115200

#define PWM_PIN         (nod_pwm_pin_t)32                   // GPIO32
#define ADC_PIN         (nod_adc1_channel_t)ADC1_CHANNEL_5  // GPIO33

#define PWM_FREQ_HZ     50
#define PWM_MIN_US      1000
#define PWM_MAX_US      2000

// TODO
#define SAMPLE_US       62   // ~16 kHz = 1 000 000 RPM
// 100 k RPM, 100 samples

#define VAL_HIST_BINS   256
#define IRQ_HIST_BINS   1024
#define REV_HIST_BINS   1024

#define PRINT_CYCLE_SEC 1.000

// ----------------------- Globals -----------------------

nod_mutex_t timer_mutex = portMUX_INITIALIZER_UNLOCKED;

volatile uint32_t sample_count = 0, crossing_count = 0;
volatile uint32_t val_hist[VAL_HIST_BINS] = {0};
volatile uint32_t irq_timing_hist[IRQ_HIST_BINS] = {0};
volatile uint32_t rev_timing_hist[REV_HIST_BINS] = {0};

uint32_t threshold_bin = 0;

// ----------------------- Utilities -----------------------

uint32_t nod_pulseUS_to_duty(uint32_t pulse_us)
{
    return (uint32_t)(
        (
            (uint64_t)pulse_us * ((1 << 16) - 1)
        ) / 20000UL
    );
}

uint32_t nod_clampRPM(uint32_t v)
{
    return (v < 1000) ? 1000 : (v > 100000) ? 100000 : v;
}

uint32_t nod_rpm_to_pulse_us(uint32_t rpm)
{
    return PWM_MIN_US + (uint32_t)(
        (
            (uint64_t)(nod_clampRPM(rpm) - 1000) * (PWM_MAX_US - PWM_MIN_US)
        ) / 99000
    );
}

// ----------------------- ESC Arming -----------------------

void nod_armESC(void)
{
    nod_printf("Arming ESC...\n");

    // Option A: standard low-high-low
    nod_pwm_write(PWM_PIN, nod_pulseUS_to_duty(PWM_MIN_US));
    nod_time_sleep_sec(2.000);
    nod_pwm_write(PWM_PIN, nod_pulseUS_to_duty(PWM_MAX_US));
    nod_time_sleep_sec(2.000);
    nod_pwm_write(PWM_PIN, nod_pulseUS_to_duty(PWM_MIN_US));
    nod_time_sleep_sec(2.000);
    nod_printf("ESC armed (standard sequence)\n");

    /*
    // Option B: simple safe-low only
    nod_pwm_write(PWM_PIN, nod_pulseUS_to_duty(PWM_MIN_US));
    nod_time_sleep_sec(3.000);
    nod_printf("ESC armed (safe-low only)\n");
    */
}

// ----------------------- ISR -----------------------

void IRAM_ATTR nod_timer_irq(void)
{
    static bool currently_above = false;

    const uint32_t start_sec = nod_time_get_sec();

    const int raw = adc1_get_raw(ADC_PIN);

    const uint32_t bin = (uint32_t)((raw*HIST_BINS)/4096);

    nod_mutex_lock_ISR(&timer_mutex);

    hist[bin]++;
    sample_count++;

    // crossing detection
    if (raw >= threshold_bin*16)
    {
        if (!currently_above)
        {
            crossing_count++;
            currently_above = true;
        }
    }
    else {
        currently_above = false;
    }

    // ISR timing profiling
    const uint32_t dur_sec = nod_time_get_sec() - start_sec;
    if (dur_sec >= 0.001 && dur_sec <= 1.000)
    {
        irq_timing_hist[duration/1000.0 - 1]++;
    }

    nod_mutex_unlock_ISR(&timer_mutex);
}

// ----------------------- Decile helper -----------------------

void nod_deciles(uint32_t *hist, int bins, int count, uint8_t *out)
{
    const uint32_t target = count / 10;
    uint32_t acc = 0, idx = 0;

    for (int d = 0; d < 10; d++)
    {
        while (idx < bins && acc < target)
        {
            acc += hist[idx++];
        }
        out[d] = idx-1;
    }
}

// ----------------------- Main -----------------------
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

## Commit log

2025-11-09 Initial commit
    * README.md, .gitignore
    * Fizeau notes
    * Foucault
    * Mechanical: mirror holder (OpenScad)
    * Electrical: PCB, datasheets/pinouts
    * Software: notes
    [mirror-holder.scad, mirror-holder.stl, project-f-B_Cu.gbr, project-f-B_Mask.gbr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]
2025-11-11 Introduce HAL (WIP)
    Next steps:
    * Introduce platform (Arduino/Linux) headers
    * Implement non blocking read on Linux
    * Implement timer on Linux
    * Implement abstraction for statistics (store samples, compute and print deciles)
    * Integrated test on Linux
    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
2025-11-12 Introduce platform (Arduino/Linux) headers and finish fixing warnings/errors
2025-11-14 Cleanup and fix the code
    * Properly implement arrays of samples, rev duration and IRQ duration with mutex handling
    * Add a few new APIs
    * Fix a few bugs
    * Timing analysis of current solution (continuous ADC sampling) shows a max of 4 k RPM
    * The requirement is absolute minimum 10 k RPM and stretch goal 100 k RPM
    * Can use GPIO IRQ, but this requires signal conditioning to digitalize the analog signal
2025-11-22 Implement Timer HAL for Linux (background thread)
    * Do more testing on Linux and fix some bugs
    * Test on HW
    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
2025-12-02 Mechanical: fix miror width, and add 3D printing details
    [mirror-holder.scad, mirror-holder.stl]
2025-12-02 Software: testing on HW, various fixes
    * Arduino: Rename .c to .ino (wtf arduino!)
    * Arduino: Create symlinks to have all the files in same folder (wtf arduino!)
    * Arduino: Typedef (`nod_stats_t`) do not work? (wtf arduino!)
    * Arduino: Delete unnecessary includes (Arduino and esp) (wtf arduino!)
    * Fix: PWM duty calculation - was rounded to 0 due to integer division
    * Improve: timer API (more human friendly, less leaky abstraction)
    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
2026-02-15 Mechanical: create Main Assembly (top + bottom)
    [bottom-assembly.stl, main-assembly.scad, top-assembly.stl]
2026-02-23 Mechanical: main assembly: fix 5 bugs
    * Laser holder diameter 12 -> 13
    * Corner holes between top and bottom assemblies -> screw holes
    * Motor holder holes -> fix
    * Mirror holder cylinder size: 50 -> 44
    * Light shafts diameter: 5 -> 3
    [main-assembly.scad]
2026-02-23 Mechanical: main assembly: add camera holder
    [main-assembly.scad]
2026-02-23 Mechanical: main assembly: update stl and png files
    [bottom-assembly.stl, top-assembly.stl]
